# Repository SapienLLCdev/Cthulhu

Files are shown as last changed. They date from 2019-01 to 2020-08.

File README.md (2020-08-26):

## Cthulhu_Shield_Arduino

Cthulhu Shield

This is a library for using the Cthulhu Shield sensory substitution/augmentation development kit created by [Sapien LLC](http://sapienllc.com/). 

If you like what you see here, you can purchase a Cthulhu Shield [here!](https://sapienllc.com/shop/)

The Cthulhu Shield is an open-source Arduino Uno and Arduino Mega compatible sensory substitution/sensory augmentation device. It uses an 18 electrode grid to tactiley display signals on the tongue. The electrodes on the array can be activated with patterns of electrical pulses to depolarize nerve membranes in the tongue to create different types of touch sensations. You can use these touch sensations to draw shapes or simple images on the tongue, feel different sound frequencies, or receive turn by turn directions with your tongue.

Additionally, the Cthulhu Shield can sense whether or not your tongue is in contact with different electrodes using capacitive sensing. You can use the Cthulhu Shield to send keystrokes to your computer, control the cursor, or even control a mobility device. 

In this repository, we have provided a number of example projects to get you started with your Cthulhu, but we encourage you to experiment and build your own senses!

There are some awesome uses of sensory substitution already out there. For more information on these uses, or sensory substitution or augmentation in general, take a look at the links below. 
* [Brainport](https://www.youtube.com/watch?v=OKd56D2mvN0)
* [Wikipedia](https://en.wikipedia.org/wiki/Sensory_substitution)
* [Hear with your tongue](https://source.colostate.edu/words-mouth-csu-device-lets-hear-tongue/)
* [TedTalk](https://www.ted.com/talks/david_eagleman_can_we_create_new_senses_for_humans?language=en)

# Repository Contents:

* [Bare Minimum](https://github.com/SapienLLCdev/Cthulhu/tree/master/examples/BareMinimum)
* [Serial Input](https://github.com/SapienLLCdev/Cthulhu/tree/master/examples/SerialInput)
* [Accelerometer Example](https://github.com/SapienLLCdev/Cthulhu/tree/master/examples/accelerometer_Cthulhu_example)
* [GPS Directions](https://github.com/SapienLLCdev/Cthulhu/tree/master/examples/directions_example)
* [Make Patterns](https://github.com/SapienLLCdev/Cthulhu/tree/master/examples/make_patterns)
* [Thermal Camera](https://github.com/SapienLLCdev/Cthulhu/tree/master/examples/mega_heat_cam_with_shield)
* [Tactile Button](https://github.com/SapienLLCdev/Cthulhu/tree/master/examples/tactile_button_example)
* [Tactile Cursor](https://github.com/SapienLLCdev/Cthulhu/tree/master/examples/tactile_cursor)
* [Leonardo Tactile Cursor](https://github.com/SapienLLCdev/Cthulhu/tree/master/examples/Leonardo_tactile_cursor)
* [Tactile Keypad](https://github.com/SapienLLCdev/Cthulhu/tree/master/examples/tactile_keypad)
* [Cthulhu Camera Demo](https://github.com/SapienLLCdev/Cthulhu/tree/master/Android%20Examples/CthulhuCameraDemo)

# Cthulhu Shield Schematic:

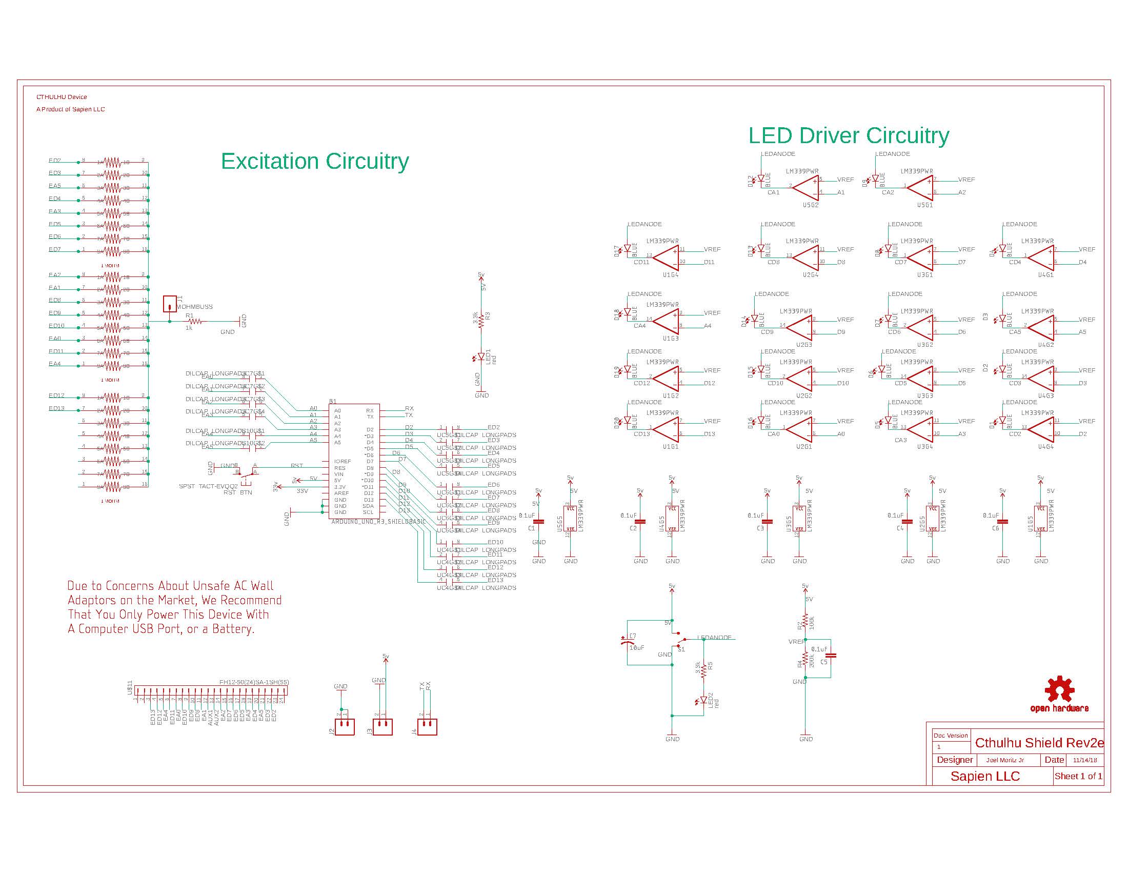
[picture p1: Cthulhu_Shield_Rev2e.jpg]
Cthulhu Shield Schematic
.

# How to Use the Cthulhu Shield:

**Power:**
The Cthulhu Shield is made to be powered by plugging it directly into an Arduino Uno or Mega, and connecting the arduino to a USB cable attached to a properly grounded computer, or a smartphone or external battery pack. Users should not power their Arduino/Cthulhu Shield system with an AC wall adaptor, as a small number of these adaptors are not properly grounded or are otherwise unsafe and can cause injury or death if used with any electronic device.

**Input:**
When used with an Arduino Uno, the Cthulhu Shield can receive information directly from the USB port connected to a computer or smartphone, or via broken out Serial pins (RX, TX) which can used to communicate with other Arduinos/microcontrollers, or embedded devices such as Bluetooth modules or sensors with serial outputs. With an Arduino Mega, the extra IO pins can be leveraged to receive Digital or Analog signals that can be used to change the tactile output of the Cthulhu Shield. 

**Output:**
When used with an Arduino Uno, the Cthulhu Shield can send information directly via USB port connected to a computer or smarptphone, or via broken out Serial pins (RX, TX) which can used to communicate with other Arduinos/microcontrollers, or embedded devices such as Bluetooth modules or sensors with serial outputs. With an Arduino Mega, the extra IO pins can be leveraged to send Digital or Analog signals to external devices. 

**Electrode Control:**
Different types of sensations can be created on different electrodes and tongue locations by changing the pattern of pulses generated on each electrode. This can be done with the Cthulhu.UpdateStimuli() function. A user changes values in six (6), eighteen (18) element arrays. The values in these arrays correspond to whether one of the 18 electrodes is on or off, and what type of pulse, and pattern of pulses, is created on each electrode. Changing these patterns changes the type and quality of the sensation perceived by the user. This library was adapted from [work by Kurt Kaczmarek](https://www.sciencedirect.com/science/article/pii/S1026309811001702) and altered for the needs of our early research at Sapien LLC.

**Tongue Position Sensing:**
During electrotactile stimulation with the Cthulhu Shield, the Arduino can quickly sense the electrical potential on a given electrode, which changes if the tongue is in contact with the electrode or not. Placing your tongue on certain electrodes but not others, or swiping your tongue across different electrodes, can be detected by the Arduino, which can then send serial information (or with minor hacking, keystrokes and HID signals) to a computer or smartphone via the USB port, or external Bluetooth modules. 

Currently, tongue-position-sensing is supported only on ADC enabled Arduino pins (A0-A5 on the Uno and Mega). Position sensing on digital only pins should be possible and may be implemented in the near future. 

# How to Use this Repository:

If you are new to Github, Sparkfun has created an [excellent Github tutorial](https://learn.sparkfun.com/tutorials/using-github/all). If you want to get up and running quickly, just take a look at the [Download ZIP](https://learn.sparkfun.com/tutorials/using-github/all#download-zip) section.

Similarly, if you are new to Arduino, Sparkfun once again has a great [guide to installing Arduino Libraries](https://learn.sparkfun.com/tutorials/installing-an-arduino-library). After downloading the .ZIP file of the library you want from Github, follow the instructions above to integrate it with the Arduino IDE.

Please see the README files in the examples linked above for more information on their specific implementations!

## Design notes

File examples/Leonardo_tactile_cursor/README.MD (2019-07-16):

## Using the Cthulhu Shield and Arduino Leonardo as a Full-Function Computer Mouse!

# Introduction:

The Cthulhu Shield and electrode array can be used to sense whether or not your tongue is in contact with certain electrodes. Combined with the electrotactile ability of the Cthulhu Shield, this can be used to create 'virtual' tactile buttons that can be pressed with the tongue. With with the HID library function of the arduino Leonardo, you can use the Cthulhu to control your computer cursor or type with your tongue!

This example will show you how to upload the example 'Leonardo_tactile_cursor.ino' sketch to an Arduino Leonardo with mounted Cthulhu Shield to use your tongue to mouse movements to your computer. You can also use the onscreen keyboard to type and send emails with your tongue! 

This example is considerably easier to use than the 'tactile_cursor' example. But requires an Arduino Leonardo.

[An video of the device being used can be found here](https://youtu.be/Bt2chGSGTl8)

[Instructions on how to control the cursor can be found here](https://github.com/SapienLLCdev/Cthulhu/blob/master/examples/Leonardo_tactile_cursor/Tongue%20mouse%20instructions.pdf)

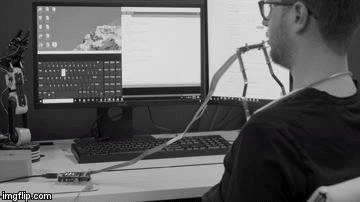
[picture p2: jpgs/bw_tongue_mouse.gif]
Game_Control


# Required Materials:

* Cthulhu Shield

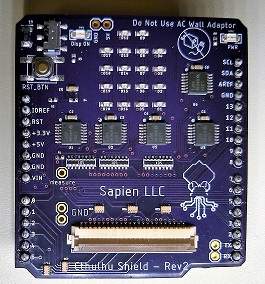
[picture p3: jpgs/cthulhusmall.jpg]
Cthulhu Shield

* Arduino Leonardo or compatible clone with Atmega32U4 microcontroller.

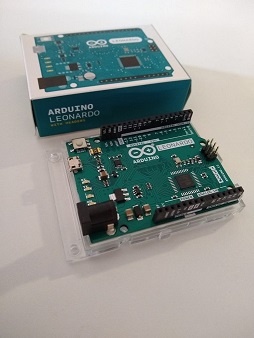
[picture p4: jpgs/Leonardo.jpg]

* USB A to B Cable

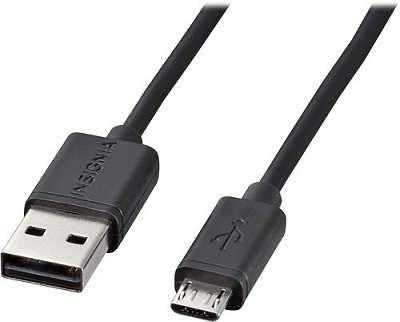
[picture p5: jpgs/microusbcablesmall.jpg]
USB A to micro B cable


* One 18 Channel flexible electrode array from Sapien LLC

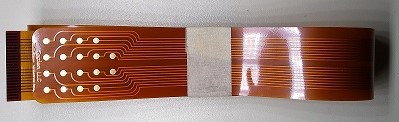
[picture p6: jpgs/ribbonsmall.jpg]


# Required Software:
* This library
* [Arduino IDE](https://www.arduino.cc/en/Main/Software)

# Hardware Assembly:
Install Cthulhu Shield onto Arduino Leonardo and attach the USB cable and electrode array. 

# PC Setup:
For setup on Windows, follow the instructions below. If you have a Mac, please see the section entitled [Mac Setup](#mac-setup) further down the page. 

Open Arduino IDE. Once you have installed the Cthulhu Shield library (see 'Install Library' at end) go to **file**>**examples**>**Cthulhu-master** and open the **Leonardo_tactile_cursor** example sketch.

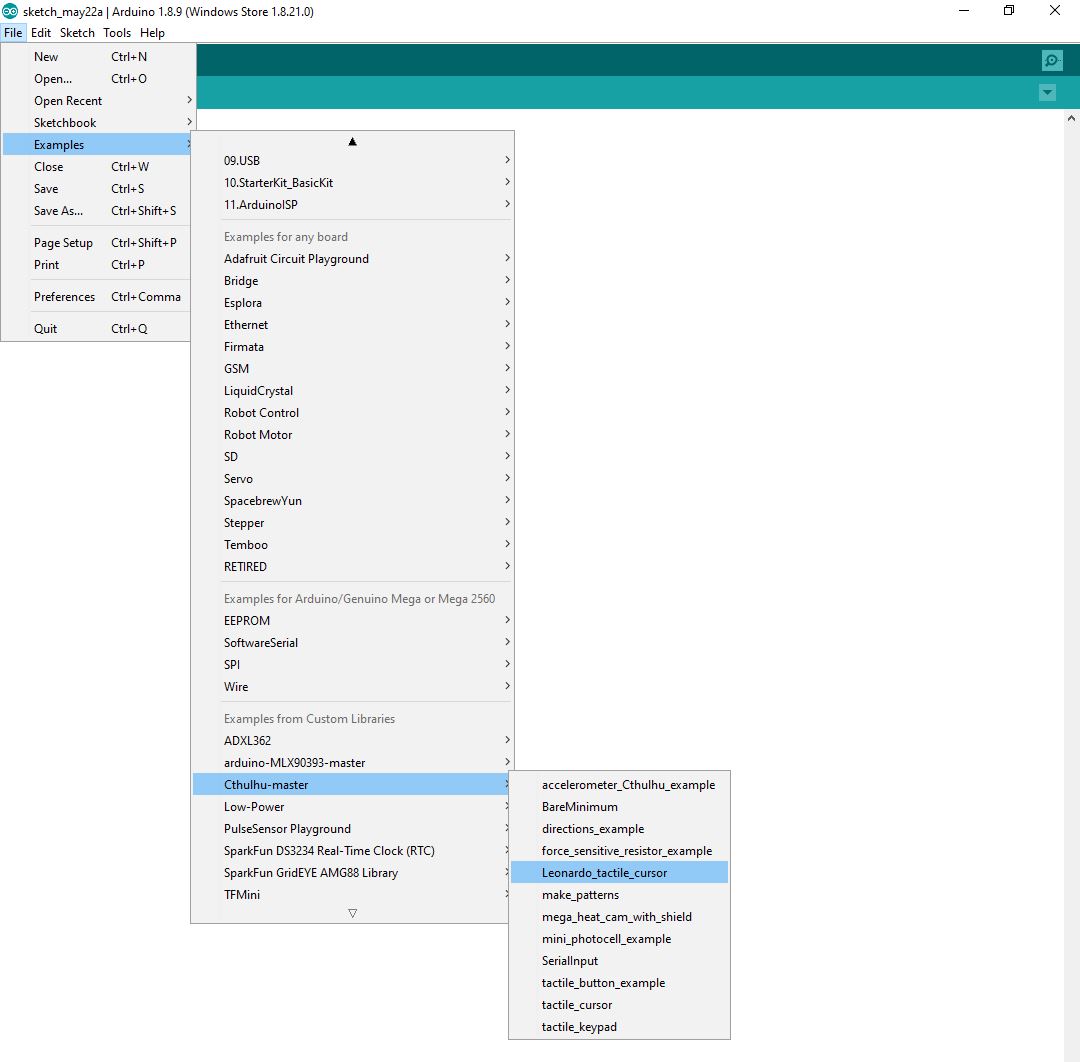
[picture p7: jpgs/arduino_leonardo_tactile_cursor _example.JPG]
example


Set your board and serial port from the **tools** dropdown menu and upload the sketch to your Arduino Leonardo.

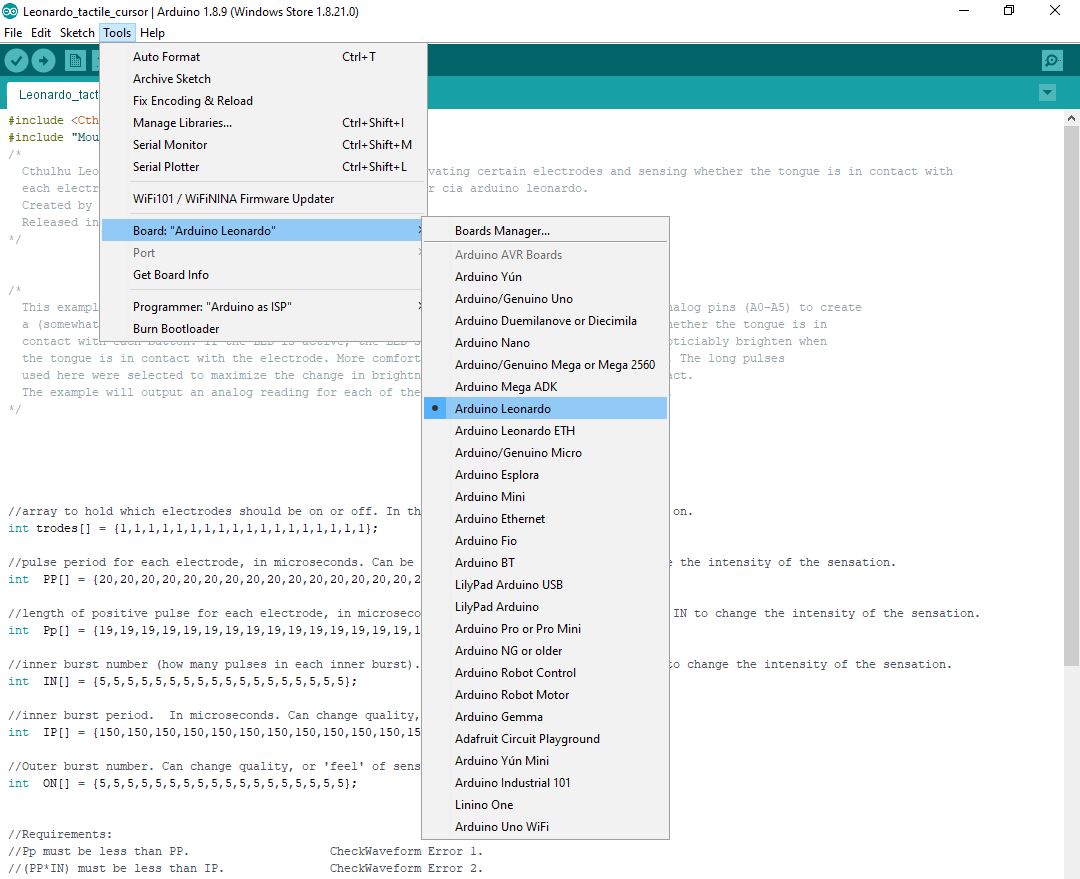
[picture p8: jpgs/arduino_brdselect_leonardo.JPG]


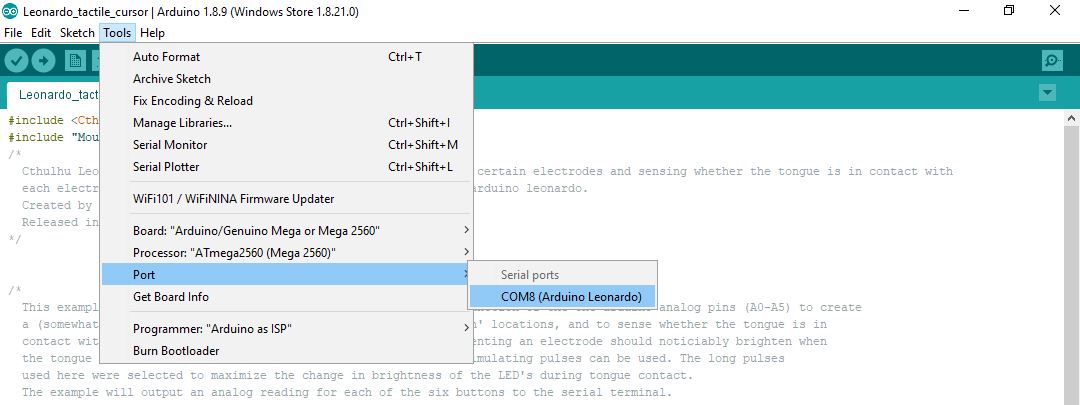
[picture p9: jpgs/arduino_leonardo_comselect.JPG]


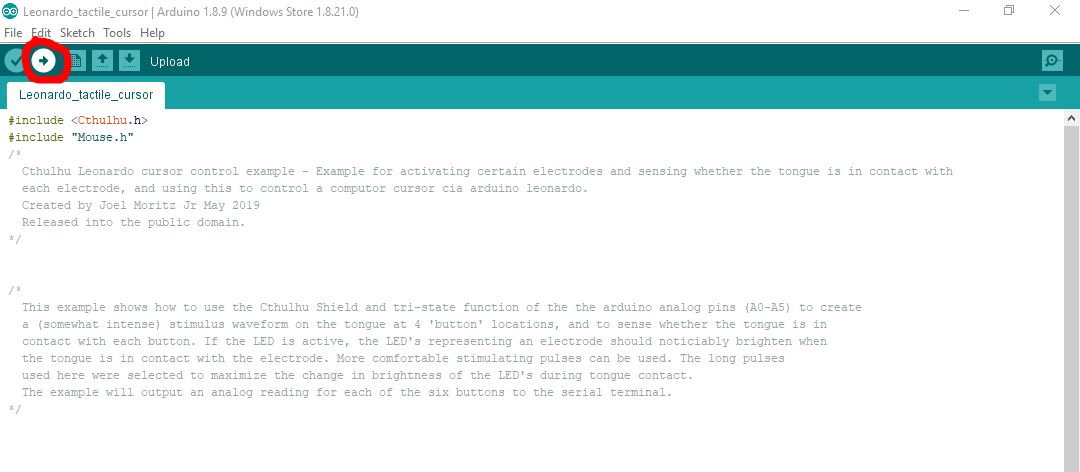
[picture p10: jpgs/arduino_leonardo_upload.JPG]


If you havent already, carefully lift the latch of the ZIF connector, insert the electrode array gold side down, and close the latch. 

* Use the tip of your tongue to press the tactile 'buttons' on the electrodes at the front, back , and both sides of the array. The LED's on the Cthulhu Shield will (very slightly) change brightness when your tongue is contacting them.
* To click, flatten your tongue against the array (and the roof of your mouth) with a slapping motion to contact all the electrodes, then pull your tongue off the array. Double clicking works similarly. Clicking will activate all LED's on the array at once to give you tactile and visual feedback.
* To right-click, flatten your tongue against all electrodes as described above, and hold your tongue against all electrodes for about 2 seconds, then release. The appropriate right-click menu should pop up when released. 
* To click-drag/click-and-hold (moving a window, or using a scrollbar, etc), Flatten your tongue against all electrodes to click, and hold your tongue against the array while sliding your tongue to the desired directional button.

You can enable the oncsreen keyboard in the windows control panel if you want to try typing with your tongue! 

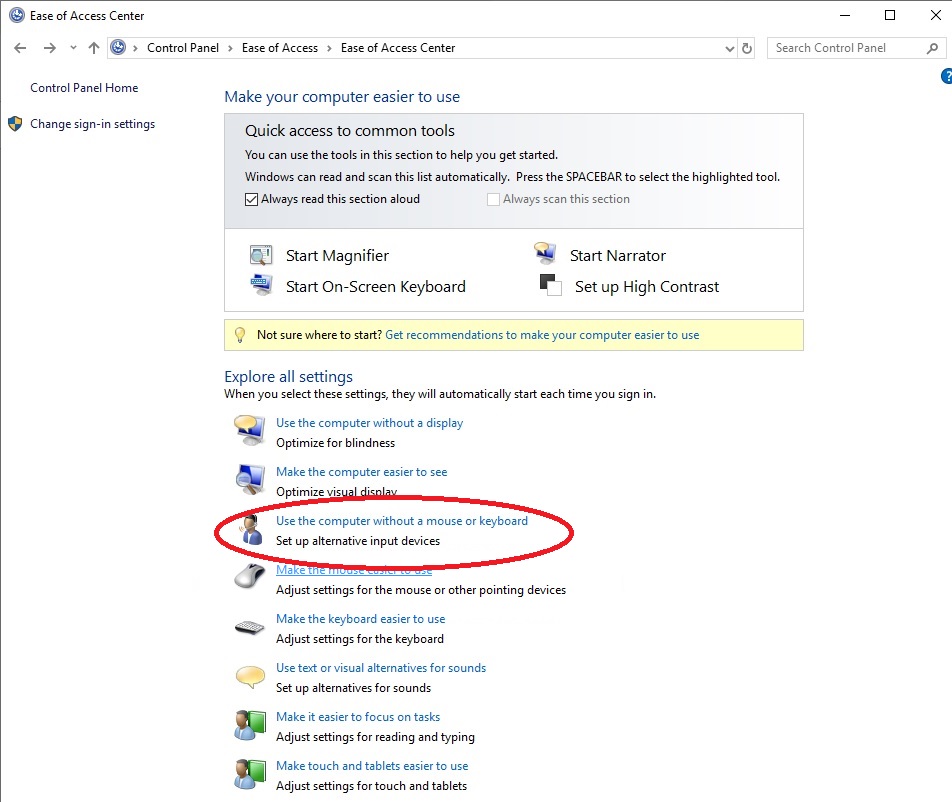
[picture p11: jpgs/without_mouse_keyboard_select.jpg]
key1


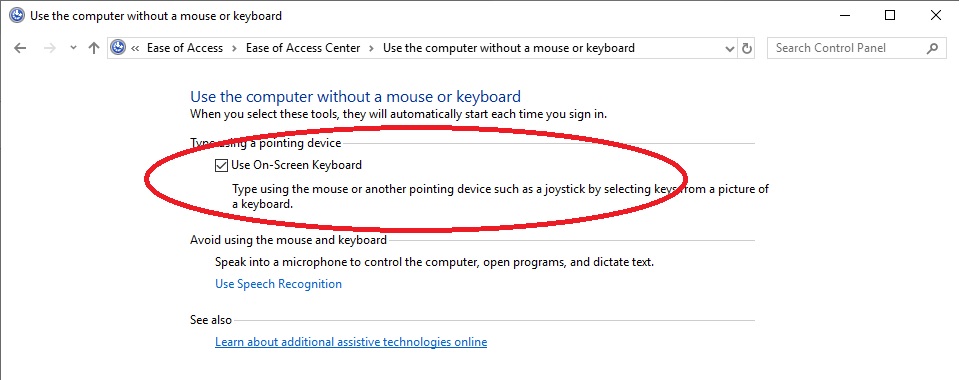
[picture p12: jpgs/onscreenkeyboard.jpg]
key2


# Going Further:

# Acknowledgments: 

# Install Library:

Right now, the easiest way to install the Cthulhu library is by downloading the Zip file from github, and manually adding it from the arduino 'sketch' dropdown menu.

Navigate to the Cthulhu repo main page and download the zip file.

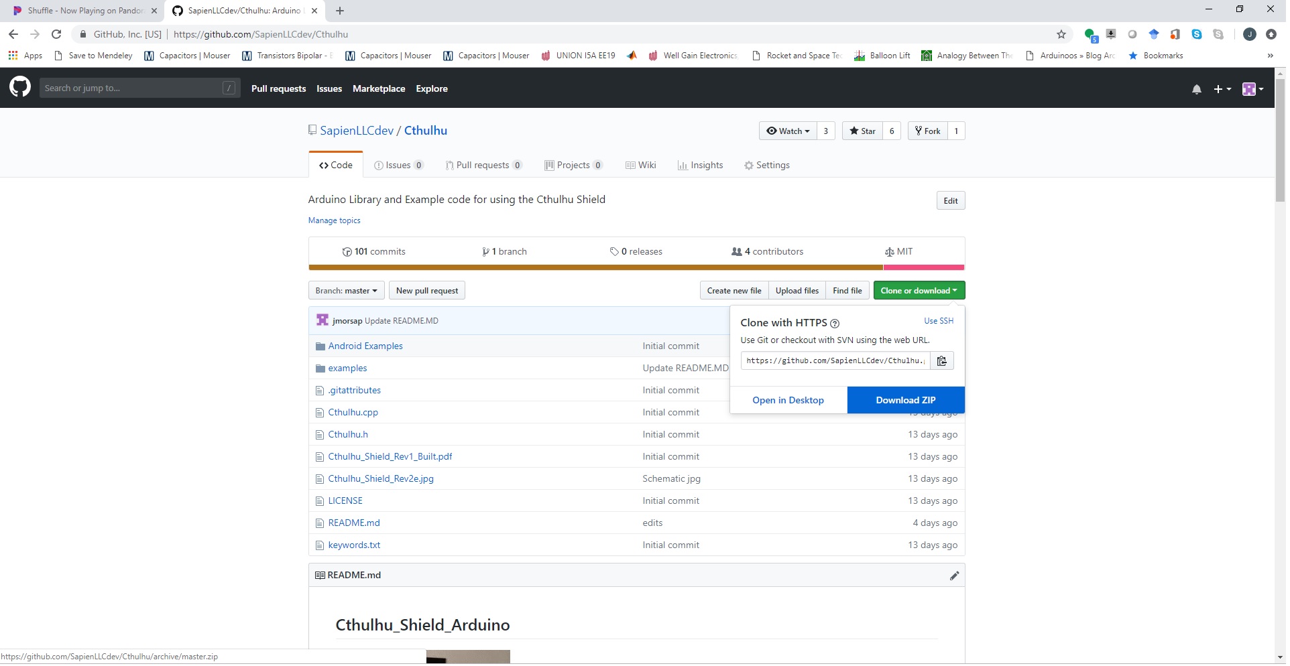
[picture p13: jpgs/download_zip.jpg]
zip


Open Arduino and select **Include Library** > **Add .ZIP Library** from the **Sketch** dropdown menu.

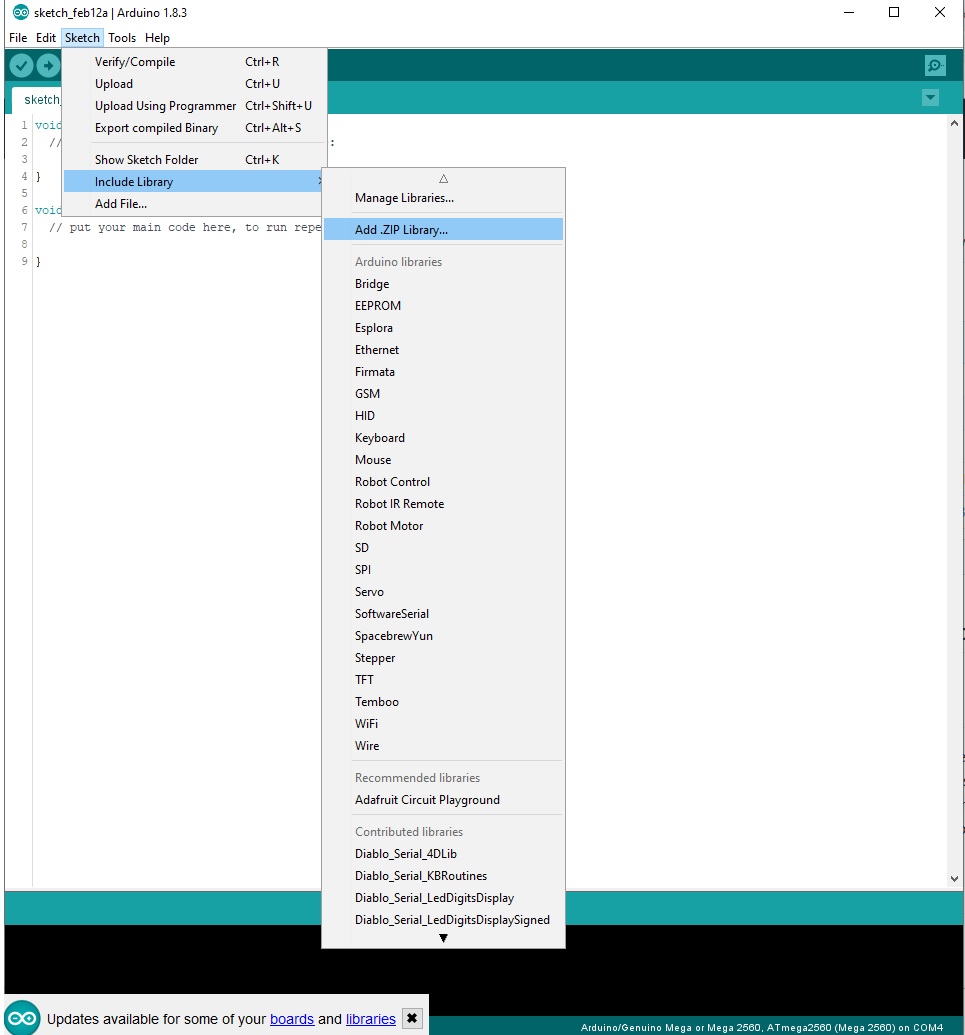
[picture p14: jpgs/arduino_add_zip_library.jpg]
add library


Navigate to the zip file you downloaded and select it (probably your 'Downloads' folder). 

The library should now be installed.

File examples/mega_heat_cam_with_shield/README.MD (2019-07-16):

## Using the Cthulhu Shield, Arduino Mega, and the SparkFun GRID-Eye Infrared Array (Qwicc) to Sense Warm Objects With Your Tongue!

# Introduction

This example illustrates the use of the Cthulhu as a sensory substitution device paired with the Quicc GRID-Eye Infrared Array to sense the warmth of objects. When a warm object is sensed by the Infrared Array, the LEDs on the Cthulhu will light up, and the corresponding electrodes on the removable flexible array will be stimulated.

# Required Materials:

* Cthulhu Shield

Cthulhu_Shield

* Arduino Mega or compatible clone

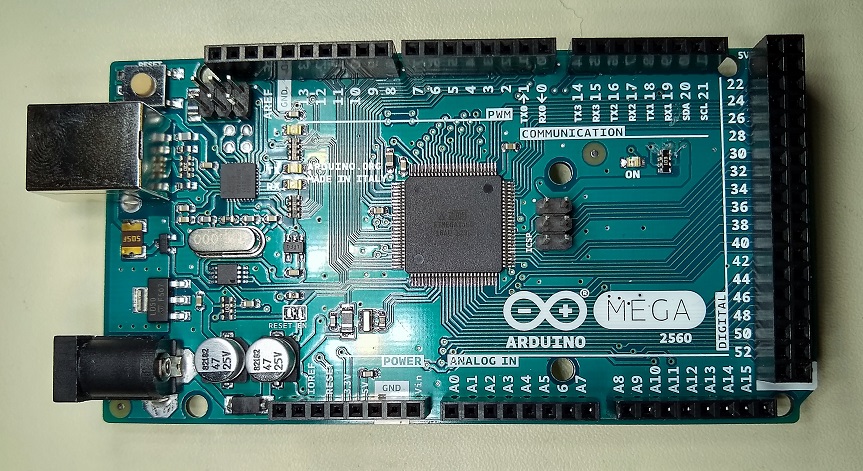
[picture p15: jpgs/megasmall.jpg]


* SparkFun Grid-EYE Infrared Array Breakout - AMG8833 (Qwiic)

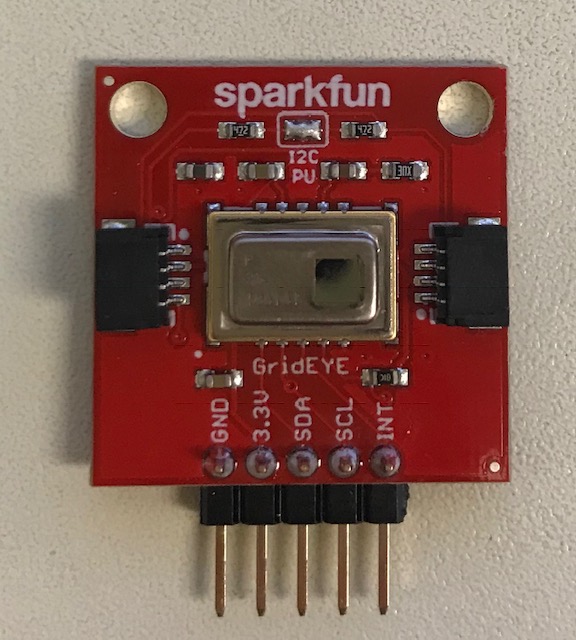
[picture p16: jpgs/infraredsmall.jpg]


* SparkFun Logic Level Converter - Bi-Directional

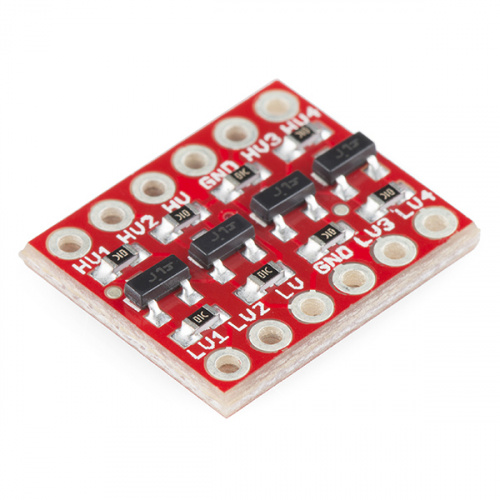
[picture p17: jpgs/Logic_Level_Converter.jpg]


* USB A to B Cable

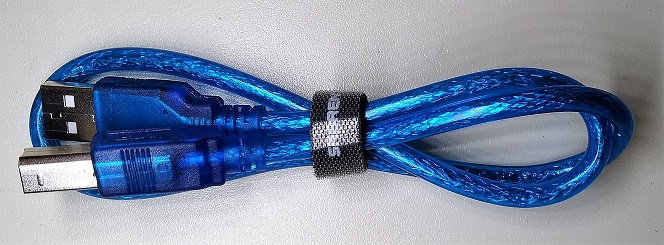
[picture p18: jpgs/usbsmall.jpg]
USB A to B Cable


* One 18 Channel flexible electrode array from Sapien LLC

Cthulhu Shield

# Required Software
* This library (Directions on how to install below)
* [Arduino IDE](https://www.arduino.cc/en/Main/Software)
* [GridEYE Library](https://github.com/sparkfun/SparkFun_GridEYE_Arduino_Library).

If you do not know how to install an Arduino library, refer to the "How to Use this Repository" section [in the README](https://github.com/SapienLLCdev/Cthulhu). 

# Hardware Assembly:
Install Cthulhu Shield onto Arduino Uno or Arduino Mega and attach the USB cable and electrode array. 

# Quicc GRID-Eye Infrared Array setup with Arduino Mega, Cthulhu Shield, and Logic Level Converter

| Cthulhu Shield/Mega | High Side of Converter | Low side of converter | Infrared Camera |
| ------------------- | ---------------------- | --------------------- | --------------- |
| 3.3V  | N/A  | LV  | 3.3V  |
| 5V  | HV  | N/A  | N/A  |
| GND  | GND  | GND  | GND  |
| Pin 20 (SDA)  | HV1  | LV1  | SDA  |
| Pin 21 (SCL)  | HV2  | LV2  | SCL  |

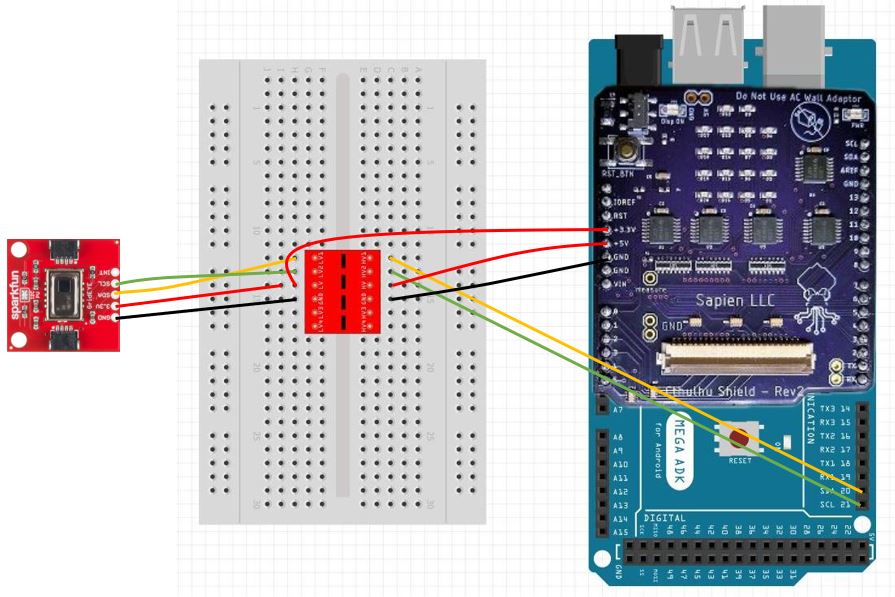
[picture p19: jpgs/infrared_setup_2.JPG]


The logic level converter is used in this example because the infrared camera uses 3.3V and the Arduino mega uses 5V. The 5V goes into the HIGH (HV) side of the converter and the 3.3V goes into the LOW (LV) side, as pictured above.

# Example:
Open Arduino IDE. Once you have installed the Cthulhu Shield library (see 'Install Library' at end) go to **file**>**examples**>**Cthulhu-master** and open the **mega_heat_cam_with_shield** example sketch.

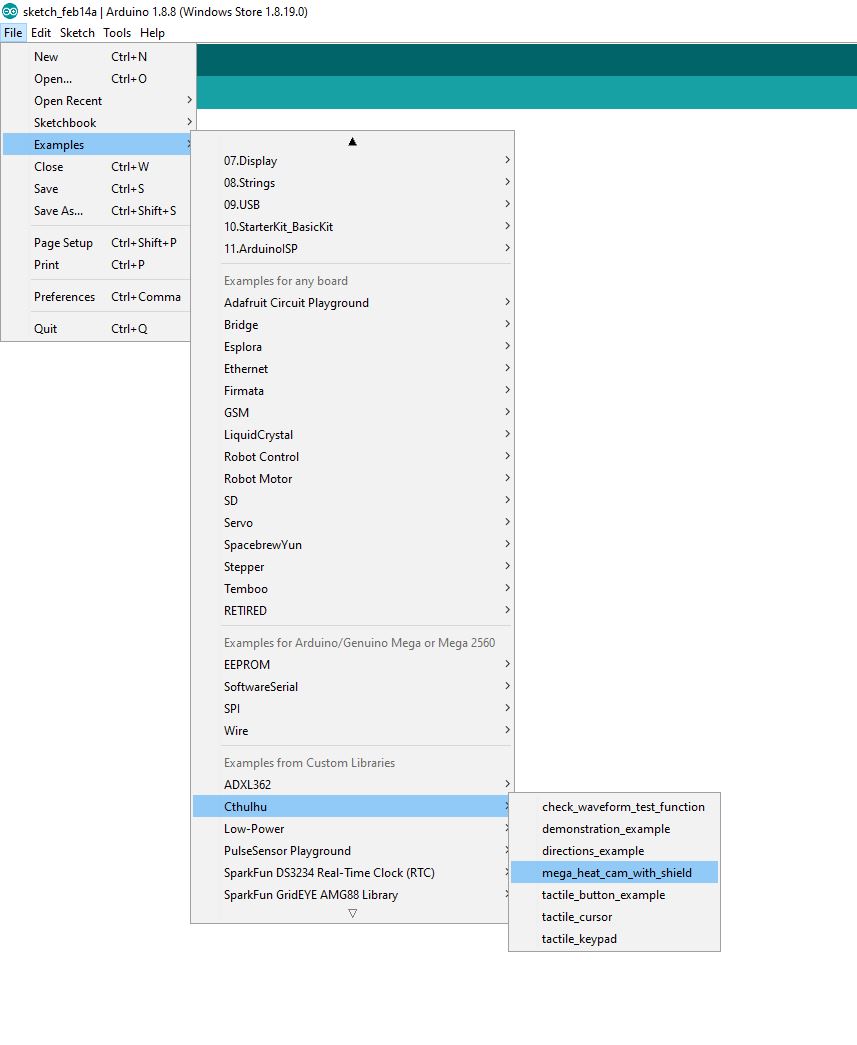
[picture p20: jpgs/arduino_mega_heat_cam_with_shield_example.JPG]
example


Set your board and serial port from the **tools** dropdown menu and upload the sketch to your Arduino Uno or Mega.

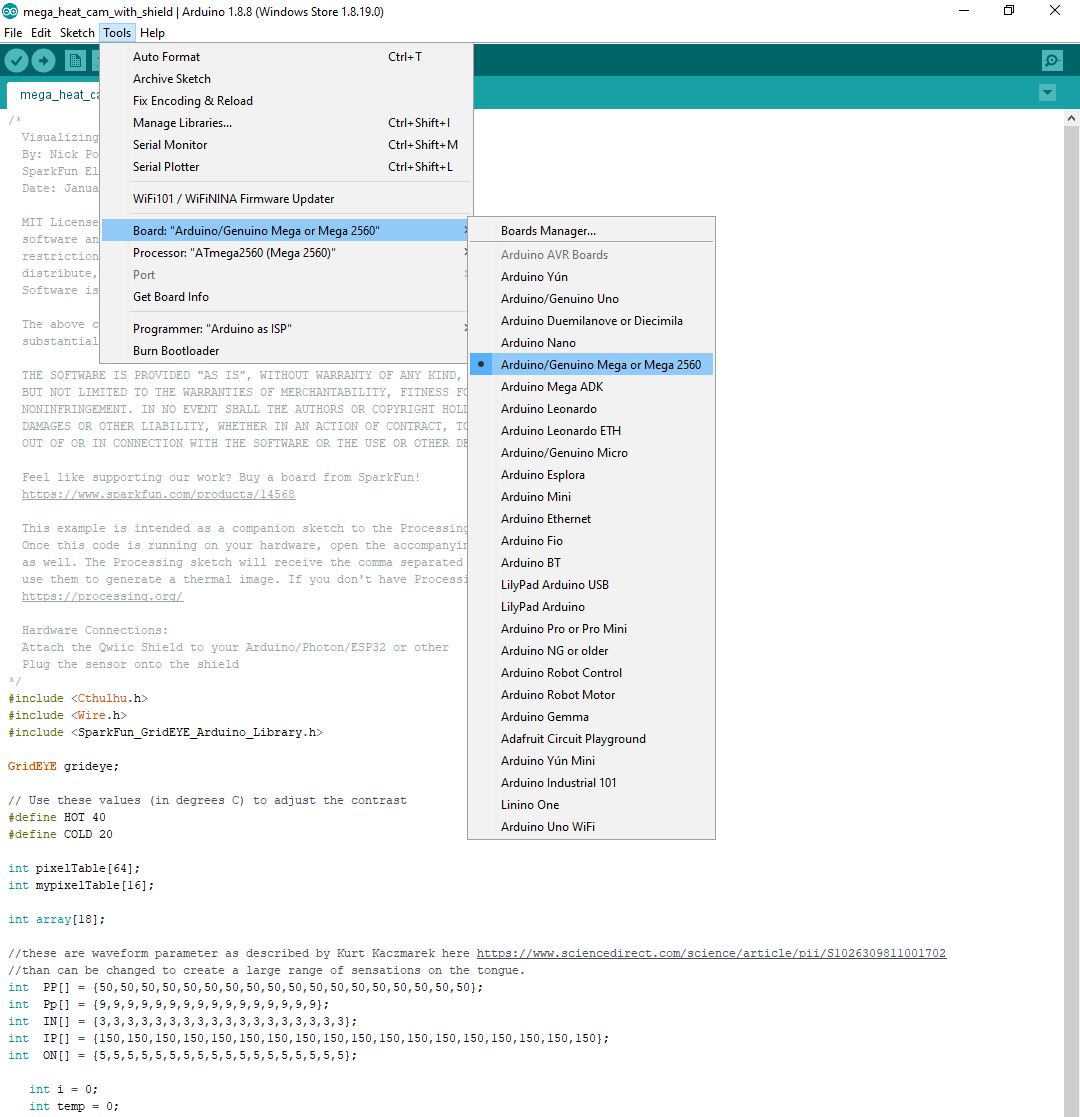
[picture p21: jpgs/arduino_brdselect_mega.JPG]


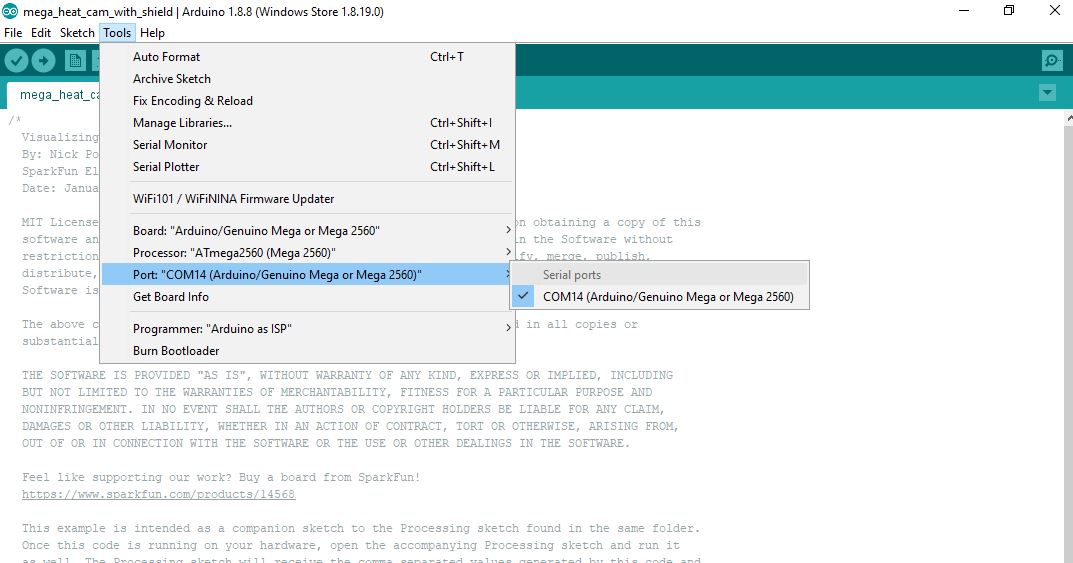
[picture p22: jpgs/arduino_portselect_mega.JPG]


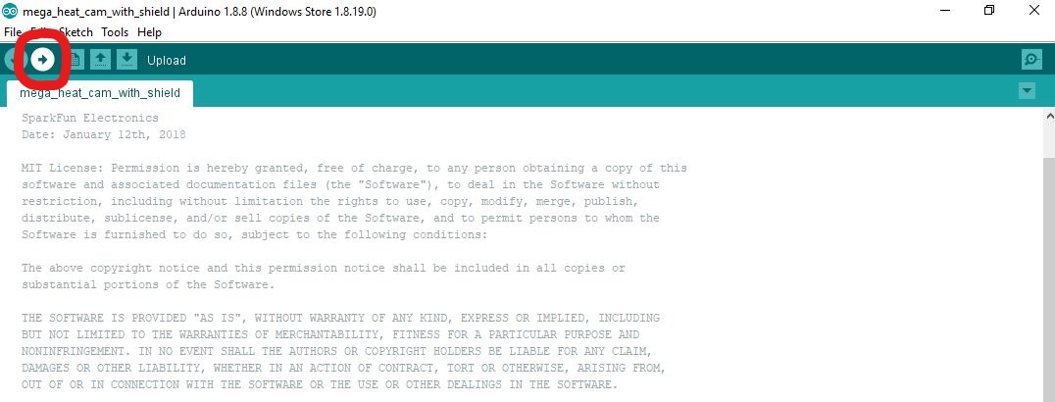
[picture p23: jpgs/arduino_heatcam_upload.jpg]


If everything has been setup correctly, when you wave a warm object (such as your hand) over the SparkFun GRID-Eye Infrared Array sensor, the LEDs on the Cthulhu Shield will respond by lighting up. If you wave a cold object over the sensor, then no LEDs will light up. If the 18 Channel flexible electrode array from Sapien LLC has been connected to the Cthulhu Shield, the electrodes on the flexible array will be stimulated in response to warm objects. 

# Install Library:

Right now, the easiest way to install the Cthulhu library is by downloading the Zip file from github, and manually adding it from the arduino 'sketch' dropdown menu.

Navigate to the Cthulhu repo main page and download the zip file.

zip

Open Arduino and select **Include Library** > **Add .ZIP Library** from the **Sketch** dropdown menu.

add library

Navigate to the zip file you downloaded and select it (probably your 'Downloads' folder). 

The library should now be installed.

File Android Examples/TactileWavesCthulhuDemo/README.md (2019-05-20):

Tactile Waves Cthulhu Demo
==========================
This app shows how the [Tactile Waves Android library](https://github.com/Funkatronics/TactileWaves "Tactile Waves") can be used with the Cthulhu Shield to build a sound-to-touch sensory substitution system.

Tactile Waves is used to capture and process audio from the devices microphone to extract its fundamental frequency (pitch) and formant frequencies. These frequencies are drawn to the screen for visualization. 

An Arduino equipped with a Cthulhu Shield can be connected to the app via USB or Bluetooth (using the 3-dot overflow menu on the app's toolbar). When connected, the formant frequencies will be mapped and sent to the Cthulhu LEDs/electrodes.

Installation
------------
The easiest way to install this app is via the Google Play Store here.~~ https://play.google.com/store/apps/developer?id=SapienLLC&hl=en_US

Alternatively, the APK provided in this folder can be installed by enabling "Unknown Sources" in your devices security settings. With this setting enabled, you will be able to open the APK file on your device and Android will begin the installation automatically. 

You can also clone this repository to a folder on your computer and build the APK yourself. 

Credits
-------
Built by Marco Martinez ([Funkatronics](https://github.com/funkatronics "Funkatronics GitHub")) with support from Sapien, LLC and CSU Ventures.

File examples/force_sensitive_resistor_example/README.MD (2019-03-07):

## Using the Cthulhu Shield, Arduino Mega, and the SparkFun Force Sensitive Resistor to Feel Changes in Force with your Tongue!

# Introduction

This example illustrates the use of the Cthulhu as a sensory substitution device paired with the SparkFun Force Sensitive Resistor to feel changes in force intensity. The greater amount of force placed on the Force Sensitive Resistor, the more intense the stimulation experience will be.

# Required Materials:

* Cthulhu Shield

Cthulhu_Shield

* Arduino Mega or compatible clone

Cthulhu Shield

* SparkFun Force Sensitive Resistor 0.5"

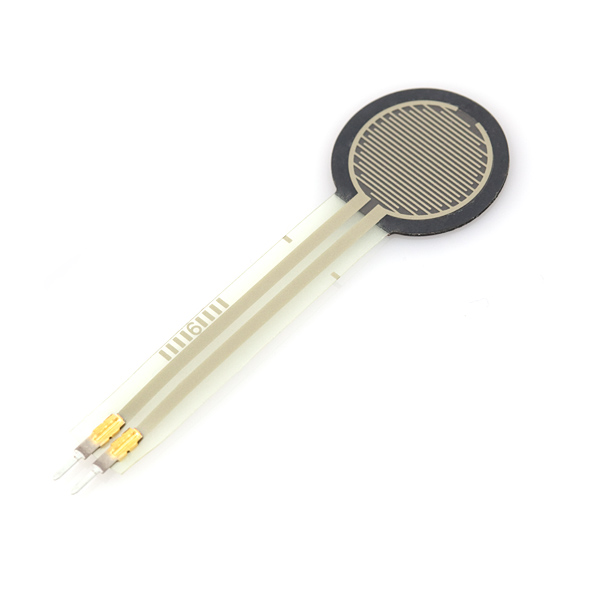
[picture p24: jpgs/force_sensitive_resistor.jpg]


* 3.3kΩ Resistor

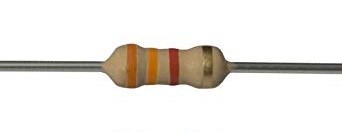
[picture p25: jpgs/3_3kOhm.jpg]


* Breadboard

Cthulhu_Shield

* USB A to B Cable

USB A to B Cable

* One 18 Channel flexible electrode array from Sapien LLC

Cthulhu Shield

# Required Software
* This library (Directions on how to install below)
* [Arduino IDE](https://www.arduino.cc/en/Main/Software)

If you do not know how to install an Arduino library, refer to the "How to Use this Repository" section [in the README](https://github.com/SapienLLCdev/Cthulhu). 

# Hardware Assembly:
Install Cthulhu Shield onto Arduino Uno or Arduino Mega and attach the USB cable and electrode array. 

# Force Sensitive Resistor Setup with Mega and Cthulhu Shield 

Cthulhu_Shield

For this example, a 3.3kΩ resistor was used. Refer to the SparkFun Force Sensitive Resistor hookup guide [here](https://learn.sparkfun.com/tutorials/force-sensitive-resistor-hookup-guide?_ga=2.62589669.834921711.1551994825-586526424.1528213955) if more reference is needed.

# Example:
Open Arduino IDE. Once you have installed the Cthulhu Shield library (see 'Install Library' at end) go to **file**>**examples**>**Cthulhu-master** and open the **force_sensitive_resistor_example** example sketch.

example

Set your board and serial port from the **tools** dropdown menu and upload the sketch to your Arduino Uno or Mega.

example

example

example

If everything has been setup correctly, when the example is uploaded, no electrodes should be stimuluated initially. Once a force is applied to the Force Sensitive Resistor, by squeezing it with your fingers for example, the electrodes will be stimulated in an "X" pattern. The greater amount of force applied (the harder you squeeze) the greater intensity of the stimulus. Once the force applied is reduced, the intensity of the stimuluation will decrease. 
 
# Install Library:

Right now, the easiest way to install the Cthulhu library is by downloading the Zip file from github, and manually adding it from the arduino 'sketch' dropdown menu.

Navigate to the Cthulhu repo main page and download the zip file.

zip

Open Arduino and select **Include Library** > **Add .ZIP Library** from the **Sketch** dropdown menu.

add library

Navigate to the zip file you downloaded and select it (probably your 'Downloads' folder). 

The library should now be installed.

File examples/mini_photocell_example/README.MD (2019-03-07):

## Using the Cthulhu Shield, Arduino Mega, and the SparkFun Mini Photocell to Feel Light with your Tongue!

# Introduction

This example illustrates the use of the Cthulhu as a sensory substitution device paired with the SparkFun Mini Photocell to feel changes in light intensity. The more intense the light on the Mini Photocell, the more intense the stimulation experience will be.

# Required Materials:

* Cthulhu Shield

Cthulhu_Shield

* Arduino Mega or compatible clone

Cthulhu Shield

* SparkFun Mini Photocell

Cthulhu_Shield

* Breadboard

Cthulhu_Shield

* 1kΩ Resistor

Cthulhu_Shield

* USB A to B Cable

USB A to B Cable

* One 18 Channel flexible electrode array from Sapien LLC

Cthulhu Shield

# Required Software
* This library (Directions on how to install below)
* [Arduino IDE](https://www.arduino.cc/en/Main/Software)

If you do not know how to install an Arduino library, refer to the "How to Use this Repository" section [in the README](https://github.com/SapienLLCdev/Cthulhu). 

# Hardware Assembly:
Install Cthulhu Shield onto Arduino Uno or Arduino Mega and attach the USB cable and electrode array. 

# Mini Photocell setup with Mega and Cthulhu Shield 

Cthulhu_Shield

For this example, a 1kΩ resistor was used. Refer to the SparkFun Mini Photocell setup guide [here](https://learn.sparkfun.com/tutorials/photocell-hookup-guide/all) if more reference is needed.

# Example:
Open Arduino IDE. Once you have installed the Cthulhu Shield library (see 'Install Library' at end) go to **file**>**examples**>**Cthulhu-master** and open the **mini_photocell_example** example sketch.

example

Set your board and serial port from the **tools** dropdown menu and upload the sketch to your Arduino Uno or Mega.

example

example

example

If everything has been setup correctly, when the example is uploaded, the electrodes should be stimulated in an "x" pattern. If the light intensity is increased on the photocell by shining a flashlight on it, for example, the intensity of the stimulus will increase. If the light intesnity is decreased by turning off the lights or putting a solid object over the photocell, for example, the intensity of the stimulus will decrease.

For this example a 1kΩ resistor was used, but a 1kΩ up to a 10kΩ resistor can be used with the photocell. Just know that changing the resistance will change the amount of voltage experienced by the photocell.
 
# Install Library:

Right now, the easiest way to install the Cthulhu library is by downloading the Zip file from github, and manually adding it from the arduino 'sketch' dropdown menu.

Navigate to the Cthulhu repo main page and download the zip file.

zip

Open Arduino and select **Include Library** > **Add .ZIP Library** from the **Sketch** dropdown menu.

add library

Navigate to the zip file you downloaded and select it (probably your 'Downloads' folder). 

The library should now be installed.

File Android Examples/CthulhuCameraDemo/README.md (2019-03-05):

Cthulhu Camera Demo
===================
This example app uses a simple frame difference method to detect motion within each frame from an Android device's front or back camera. This motion is then mapped to the 4x4 grid of electrodes on the Cthulhu Shield, connected via USB.

An evenly spaced 4x4 grid is drawn over the video stream. If the amount of motion (the difference between the previous and current frame) within one tile of the grid exceeds a threshold value, the cooresponding LED/electrode on the Cthulhu is activated. The user can adjust this threshold value using the 3-dot overflow menu on the apps toolbar. Lower threshold values will make the motion detection more sensitive (a smaller amount of motion will trigger an electrode). 

Installation
------------
The easiest way to install this app is via the Google Play Store, [here](https://play.google.com/store/apps/details?id=funkatronics.code.cthulhucamerademo&hl=en "CthulhuCameraMotionDemo")

Alternatively, the APK provided in this folder can be installed by enabling "Unknown Sources" in your devices security settings. With this setting enabled, you will be able to open the APK file on your device and Android will begin the installation automatically. 

You can also clone this repository to a folder on your computer and build the APK yourself. 

Credits
-------
Built by Marco Martinez ([Funkatronics](https://github.com/funkatronics "Funkatronics GitHub")) with support from Sapien, LLC

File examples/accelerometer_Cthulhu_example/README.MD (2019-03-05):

## Using the Cthulhu Shield, Arduino Mega, and the SparkFun Triple Axis Accelerometer to Feel Movement With Your Tongue!

# Introduction

This example illustrates the use of the Cthulhu Shield as a sensory substitution device paired with the SparkFun Triple Axis Accelerometer to feel movement on the positive and negative X and Y axes. When the accelerometer is moved in the positive or negative direction of the axes, the corresponding electrodes on the removable flexible array will be stimulated.

# Required Materials:

* Cthulhu Shield

Cthulhu_Shield

* Arduino Mega or compatible clone

Cthulhu Shield

* SparkFun Triple Axis Accelerometer Breakout - ADXL362

Cthulhu_Shield

* USB A to B Cable

USB A to B Cable

* One 18 Channel flexible electrode array from Sapien LLC

Cthulhu Shield

# Required Software
* This library (Directions on how to install below)
* [Arduino IDE](https://www.arduino.cc/en/Main/Software)
* [ADXL362](https://github.com/annem/ADXL362)

If you do not know how to install an Arduino library, refer to the "How to Use this Repository" section [in the README](https://github.com/SapienLLCdev/Cthulhu). 

# Hardware Assembly:
Install Cthulhu Shield onto Arduino Uno or Arduino Mega and attach the USB cable and electrode array. 

# Triple Axis Accelerometer setup with mega and Cthulhu Shield 

On Triple Axis Accelerometer  |    On Cthulhu Shield/Arduino MEGA
-----------------------------|----------------------------------
GND	            			 |              GND
V+	           				 |             3.3V
SCK	           				 |            Pin 52
MOSI	      				 |            Pin 51
MISO						 |			Pin 50
CS              			 |				Pin 53

* Labeled Pins on Triple Axis Accelerometer

Cthulhu_Shield

* Full Setup

Cthulhu_Shield

# Example:
Open Arduino IDE. Once you have installed the Cthulhu Shield library (see 'Install Library' at end) go to **file**>**examples**>**Cthulhu-master** and open the **accelerometer_Cthulhu_example** example sketch.

example

Set your board and serial port from the **tools** dropdown menu and upload the sketch to your Arduino Uno or Mega.

example

example

example

If everything has been setup correctly, when the example is uploaded, if the accelerometer is tilted up towards the user (+X), down away from the user (-X), down to the right (+Y), and down toward the left (-Y), the corresponding elecrodes will be stimulated. This allows for the user to feel the movement in the different directions with their tongue. The further in the direction the accelerometer is tilted, the more intense feeling the stimulation will be. 

Tilted Axis  |  Stimulated Electrodes
-----------------------------|----------------------------------
+X	            			 |                3, 4
-X	           				 |               15, 16
+Y	           				 |              9, 13
-Y	      				 |              6, 10

* Electrode Numbers on the Cthulhu Shield
<pre>
	{   0, 1   },
	{2, 3, 4, 5},
	{6, 7, 8, 9},
	{10,11,12,13},
	{14,15,16,17}
</pre>

# Install Library:

Right now, the easiest way to install the Cthulhu library is by downloading the Zip file from github, and manually adding it from the arduino 'sketch' dropdown menu.

Navigate to the Cthulhu repo main page and download the zip file.

zip

Open Arduino and select **Include Library** > **Add .ZIP Library** from the **Sketch** dropdown menu.

add library

Navigate to the zip file you downloaded and select it (probably your 'Downloads' folder). 

The library should now be installed.

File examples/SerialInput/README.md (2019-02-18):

## Activing Electrodes on the Cthulhu Shield Electrode Array Using Serial Input

# Introduction
This example shows how to activate electrodes on the Cthulhu Shield electrode array using serial input (from USB port, or an external device like a bluetooth module or another arduino).

Stimulation parameters are pre-set, and the serial input simply turns different electrodes on or off.

This eample works with the CthulhuCameraMotionDemo android app available on the android store: 
(https://play.google.com/store/apps/details?id=funkatronics.code.cthulhucamerademo) and the Cthulhu Tactile waves demo app soon to be available.

# Required Materials:

* Cthulhu Shield

Cthulhu_Shield

* Arduino Uno or compatible clone

Cthulhu Shield

* USB A to B Cable

USB A to B Cable

* One 18 Channel flexible electrode array from Sapien LLC

Cthulhu Shield

# Required Software
* [Arduino IDE](https://www.arduino.cc/en/Main/Software)
* This library (Directions on how to install below)
* [Coolterm-optional](http://freeware.the-meiers.org/)

# Hardware Assembly:
Install Cthulhu Shield onto Arduino Uno or Arduino Mega and attach the USB cable and electrode array. 

# Example:
Open Arduino IDE. Once you have installed the Cthulhu Shield library (see 'Install Library' at end) go to **file**>**examples**>**Cthulhu-master** and open the **SerialInput** example sketch.

example

Set your board and serial port from the **tools** dropdown menu and upload the sketch to your Arduino Uno or Mega.

example

example

The Serial Input example is ready to be uploaded.

example

Next, the app CoolTerm.exe can be used to activate individual electrodes on the Cthulhu. After opening CoolTerm, connect to the serial port.

example

Open the **Send String** window by going to **connection**>**Send String**. The Send String window will now be displayed.

example

In the Send String window, select **Hex**.

example

You can now manually input with hexadecimal numbers which electrodes you'd like to active. There are electrodes 1-18.

Hexadecimal and Decimal Numbers
--------------------------------
    01 = 1     |      0a = 10
	02 = 2     |      0b = 11                
    03 = 3     |      0c = 12
    03 = 3     |      0d = 13
    04 = 4     |      0e = 14
    05 = 5     |      0f = 15
    06 = 6     |      10 = 16
    07 = 7     |      11 = 17
    08 = 8     |      12 = 18
    09 = 9

For example: If you type 01 02 03 0a 12 00 and press **Send**, it will turn on electrodes 0, 1, 2, 9, and 17 in the array. 
Always include 00 at the end of the string.

example

To deactive all electrodes type **00 00** and press send.

# Install Library:

Right now, the easiest way to install the Cthulhu library is by downloading the Zip file from github, and manually adding it from the arduino 'sketch' dropdown menu.

Navigate to the Cthulhu repo main page and download the zip file.

zip

Open Arduino and select **Include Library** > **Add .ZIP Library** from the **Sketch** dropdown menu.

add library

Navigate to the zip file you downloaded and select it (probably your 'Downloads' folder). 

The library should now be installed.

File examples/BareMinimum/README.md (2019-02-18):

## How to Use Sapien LLC's Cthulhu Shield to Electrotactiley Stimulate the Tongue

# Introduction
This example shows how to use Sapien LLC's Cthulhu Sheild to electrotactiley stimulate the tongue. In this example, one electrode is set active, and five stimulation parameters are set. The Cthulhu library is initialized, and serial output is enabled. 
  
The CheckWaveform function is used to verify that we have entered a valid waveform for all electrodes, if the paramters we entered are OK, then the stimulus waveform is updated (UpdateStimuli), and the pulsetrain is sent to the active electrodes (Stimulate) for one stimulation cycle (36ms). 

If the waveform is invalid, the error code is printed to the serial monitor and the stimulus is not updated or produced. 

This loops indefinitely.

# Required Materials:

* Cthulhu Shield

Cthulhu_Shield

* Arduino Uno or compatible clone

Cthulhu Shield

* USB A to B Cable

USB A to B Cable

* One 18 Channel flexible electrode array from Sapien LLC

Cthulhu Shield

# Required Software
* [Arduino IDE](https://www.arduino.cc/en/Main/Software)
* This library (Directions on how to install below)

# Hardware Assembly:
Install Cthulhu Shield onto Arduino Uno or Arduino Mega and attach the USB cable and electrode array. 

# Example:
Open Arduino IDE. Once you have installed the Cthulhu Shield library (see 'Install Library' at end) go to **file**>**examples**>**Cthulhu-master** and open the **BareMinimum** example sketch.

example

Set your board and serial port from the **tools** dropdown menu and upload the sketch to your Arduino Uno or Mega.

example

example

The Serial Input example is ready to be uploaded.

example

After the example is uploaded, one electrode should be activated. 

# Install Library:

Right now, the easiest way to install the Cthulhu library is by downloading the Zip file from github, and manually adding it from the arduino 'sketch' dropdown menu.

Navigate to the Cthulhu repo main page and download the zip file.

zip

Open Arduino and select **Include Library** > **Add .ZIP Library** from the **Sketch** dropdown menu.

add library

Navigate to the zip file you downloaded and select it (probably your 'Downloads' folder). 

The library should now be installed.

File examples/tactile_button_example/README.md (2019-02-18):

## Using the Cthulhu Shield and Arduino Uno as a Tactile Button With Your Tongue

# Introduction:
This example shows how to use the Cthulhu Shield and tri-state function of the the arduino analog pins (A0-A5) to create a (somewhat intense) stimulus waveform on the tongue at 4 'button' locations, and to sense whether the tongue is in contact with each button. 

If the LED is active, the LED's representing an electrode should noticiably brighten when the tongue is in contact with the electrode. 

The long pulses used here were selected to maximize the change in brightness of the LED's during tongue contact. 

The example will output an analog reading for each of the six buttons to the serial terminal if desired.

# Required Materials:

* Cthulhu Shield

Cthulhu_Shield

* Arduino Uno or compatible clone

Cthulhu Shield

* USB A to B Cable

USB A to B Cable

* One 18 Channel flexible electrode array from Sapien LLC

Cthulhu Shield

# Required Software
* [Arduino IDE](https://www.arduino.cc/en/Main/Software)
* This library (Directions on how to install below)

# Hardware Assembly:
Install Cthulhu Shield onto Arduino Uno or Arduino Mega and attach the USB cable and electrode array. 

# Example:
Open Arduino IDE. Once you have installed the Cthulhu Shield library (see 'Install Library' at end) go to **file**>**examples**>**Cthulhu-master** and open the **tactile_button_example** example sketch.

example

Set your board and serial port from the **tools** dropdown menu and upload the sketch to your Arduino Uno or Mega.

example

example

example

After uploading to the arduino, when you place the 18 Channel flexible electrode array on your tongue and press with your tongue on the top, bottom, left, or right, if the LED is active, an electrode should noticiably brighten with your tongue in contact with the electrode. This example will output an analog reading, so if you'd like to view this reading, press the "serial monitor" icon on the top right side of arduino screen and the serial monitor will display those readings. 

# Install Library:

Right now, the easiest way to install the Cthulhu library is by downloading the Zip file from github, and manually adding it from the arduino 'sketch' dropdown menu.

Navigate to the Cthulhu repo main page and download the zip file.

zip

Open Arduino and select **Include Library** > **Add .ZIP Library** from the **Sketch** dropdown menu.

add library

Navigate to the zip file you downloaded and select it (probably your 'Downloads' folder). 

The library should now be installed.

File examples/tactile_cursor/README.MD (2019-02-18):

## Using the Cthulhu Shield and Arduino Uno to Send Keystrokes With Your Tongue!

# Introduction:

The Cthulhu Shield and electrode array can be used to sense whether or not your tongue is in contact with certain electrodes. Combined with the electrotactile ability of the Cthulhu Shield, this can be used to create 'virtual' tactile buttons that can be pressed with the tongue. With some minor software hacking of the Arduino, and use of Microsoft's accessibility tools, you can use the Cthulhu to control your computer cursor or type with your tongue!

This example will show you how to upload the example 'tactile_cursor.ino' sketch to an Arduino Uno with mounted Cthulhu Shield (and then hack the Arduino) to use your tongue to send '8''4''2''6' and '5' keystrokes to your computer. These keys can be used to control your computer cursor after enabling accessibility functions on your Mac or PC. You can also use the onscreen keyboard to type and send emails with your tongue!

Game_Control

# Required Materials:

* Cthulhu Shield

Cthulhu Shield
* Arduino Uno or Mega or compatible clone with Atmega16U2 as USB to UART converter (it sounds like older boards using the Atmega8U2 may also work)

Cthulhu Shield
* USB A to B Cable

USB A to B Cable

* One 18 Channel flexible electrode array from Sapien LLC

Cthulhu Shield

# Required Software:
* This library
* [Arduino IDE](https://www.arduino.cc/en/Main/Software)
* [Flip programmer](https://www.microchip.com/developmenttools/ProductDetails/flip)

# Hardware Assembly:
Install Cthulhu Shield onto Arduino Uno or Arduino Mega and attach the USB cable and electrode array. 

# PC Setup:
For setup on Windows, follow the instructions below. If you have a Mac, please see the section entitled [Mac Setup](#mac-setup) further down the page. 

Open Arduino IDE. Once you have installed the Cthulhu Shield library (see 'Install Library' at end) go to **file**>**examples**>**Cthulhu-master** and open the **tactile_cursor** example sketch.

example

Set your board and serial port from the **tools** dropdown menu and upload the sketch to your Arduino Uno or Mega.

example

example

example

Once you have downloaded the [Flip programmer](https://www.microchip.com/developmenttools/ProductDetails/flip), open the progam and select the ATmega16U2 device by selecting the IC icon in the upper left of the window. 

flipchipselect

With the Arduino powered, momentarily short these two pins together with a screwdriver or something metallic to put the ATmega16U2 into a state that allows to reprogram it.

Unohack

Click the USB cable icon in the upper left and select the 'USB' option from the dropdown. 

USB

Previously 'greyed-out' features in the window should now be available (if you can't connect and get an error message see section below titled 'Troubleshooting-Update Driver')

Select the Load HEX file button at the top of the window and navigate to and select the 'Arduino-keyboard-0.3.hex' file on your computer (located in the '16u2_firmware' folder of this example)

load hex

Once the firmware is selected, hit run to upload the new firmware to the ATmega16U2 chip on the Arduino.

run

**Now unplug your Arduino from your computer to remove power and plug it back in again. Your computer should now recognize the arduino as a standard keyboard.**

Click on your windows search bar and search for and open 'control panel'.
controlpanel

Select 'Ease of Access', and click 'Ease of Access' again in the window that opens.

ease1

ease2

Click **Make the mouse easier to use** and click the box to enable **Turn on mouse keys**.

mouse1

mouse2

We recommend adjusting the speed and acceleration of the mouse to higher settings. To do this, go back to the main **Make the mouse easier to use** menu and select **Set up mouse keys** (note, the box to enable mouse keys should already be enabled).

mouse3

Adjust the sliders as desired. We recommend max speed and medium-high acceleration.

mouse4

If you havent already, carefully lift the latch of the ZIF connector, insert the electrode array gold side down, and close the latch. 

Use the tip of your tongue to press the tactile 'buttons' on the electrodes at the front, back , and both sides of the array. The LED's on the Cthulhu Shield will change brightness when your tongue is contacting them, so look at them and move your tongue around to train up and practice. 

Use these buttons like a directional pad to move your cursor around the screen. Flatten your tongue against the array to press all electrodes to click. (click-hold/drag has not yet been implemented).

When you feel like it, enable the onscreen keyboard in the ease of access settings and type and email or novel. The predicted words suggessted at the top of the keyboard actual make typing pretty fast in most situations!

key1

key2

**Note: If you want your Arduino to act like a regular Arduino again (so you can load different sketches on it) you must short the pins together and repeat this process, selecting 'Arduino-usbserial-uno.hex' or 'Arduino-subserial-mega.hex'to put the standard Arduino firmware back onto the ATmega16U2.**

# Mac Setup:

# Going Further:

# Acknowledgments: 
Inspiration for this project and Firmware for Atmega16U2 came directly from coopermaa at https://github.com/coopermaa/USBKeyboard

# Troubleshooting-Update Driver:
If you get an error message when trying to connect to your device in Flip, you may need to update the driver in your device manager. 

Make sure you are running java Runtime Environment 32, then go to **device manager** on your computer, find the 16U2 device, 

16U2device

right click and select **properties** > **update drivers**, **browse my computer for driver software** and navigate to and select the **Flip folder** on your computer. 

16U2device2

16U2device2

16U2device2

Once the **Flip folder** has been selected, click **update drivers**.

16U2device2

# Install Library:

Right now, the easiest way to install the Cthulhu library is by downloading the Zip file from github, and manually adding it from the arduino 'sketch' dropdown menu.

Navigate to the Cthulhu repo main page and download the zip file.

zip

Open Arduino and select **Include Library** > **Add .ZIP Library** from the **Sketch** dropdown menu.

add library

Navigate to the zip file you downloaded and select it (probably your 'Downloads' folder). 

The library should now be installed.

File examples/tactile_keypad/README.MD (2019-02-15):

## Using the Cthulhu Shield and Arduino Uno to Send Keystrokes With Your Tongue!

# Introduction:

The Cthulhu Shield and electrode array can be used to sense whether or not your tongue is in contact with certain electrodes. Combined with the electrotactile ability of the Cthulhu Shield, this can be used to create 'virtual' tactile buttons that can be pressed with the tongue. With some minor software hacking of the Arduino, we can get the Arduino-Cthulhu to tell the computer that it is a keyboard and send keystrokes to your computer with your tongue.

This example will show you how to upload the example 'tactile_keypad.ino' sketch to an Arduino Uno with mounted Cthulhu Shield (and then hack the Arduino) to  use your tongue to send 'w''a''s''d' and 'space' keystrokes to your computer. These keys are the standard keys used to control character movement in many PC games, thus you will be able to move your character with your tongue as shown in the gif below.

Game_Control

# Required Materials:

* Cthulhu Shield

Cthulhu Shield
* Arduino Uno or Mega or compatible clone with Atmega16U2 as USB to UART converter (it sounds like older boards using the Atmega8U2 may also work)

Cthulhu Shield
* USB A to B Cable

USB A to B Cable

* One 18 Channel flexible electrode array from Sapien LLC

Cthulhu Shield

# Required Software:
* This library
* [Arduino IDE](https://www.arduino.cc/en/Main/Software)
* [Flip programmer](https://www.microchip.com/developmenttools/ProductDetails/flip)

# Hardware Assembly:
Install Cthulhu Shield onto Arduino Uno or Arduino Mega and attach the USB cable and electrode array. 

# Example:
Open Arduino IDE. Once you have installed the Cthulhu Shield library (see 'Install Library' at end) go to **file**>**examples**>**Cthulhu-master** and open the **tactile_keypad** example sketch.

example

Set your board and serial port from the **tools** dropdown menu and upload the sketch to your Arduino Uno or Mega.

example

example

example

Once you have downloaded the [Flip programmer](https://www.microchip.com/developmenttools/ProductDetails/flip), open the progam and select the ATmega16U2 device by selecting the IC icon in the upper left of the window. 

flipchipselect

With the Arduino powered, momentarily short these two pins together with a screwdriver or something metallic to put the ATmega16U2 into a state that allows to reprogram it.

Unohack

Click the USB cable icon in the upper left and select the 'USB' option from the dropdown. 

USB

Previously 'greyed-out' features in the window should now be available (if you can't connect and get an error message see section below titled 'Troubleshooting-Update Driver')

Select the Load HEX file button at the top of the window and navigate to and select the 'Arduino-keyboard-0.3.hex' file on your computer (located in the '16u2_firmware' folder of this example)

load hex

Once the firmware is selected, hit run to upload the new firmware to the ATmega16U2 chip on the Arduino.

run

**Now unplug your Arduino from your computer to remove power and plug it back in again. Your computer should now recognize the arduino as a standard keyboard.**

If you havent already, carefully lift the latch of the ZIF connector, insert the electrode array gold side down, and close the latch. Open a text editor and place the electrode array in your mouth to test it out. 

Use the tip of your tongue to press the tactile 'buttons' on the electrodes at the front, back , and both sides of the array. The LED's on the Cthulhu Shield will change brightness when your tongue is contacting them, so look at them and move your tongue around to train up and practice. 'w', 'a', 's', and 'd' keystrokes are mapped to the front, left, back, and right electrodes respectively. A 'space' keystroke can be sent by flattening your tongue against the array and pressing all the electrodes simultaneously. 

When you feel like it, fire up your favorite game with 'wasd' motion control and try controlling your character with your tongue!

**Note: If you want your Arduino to act like a regular Arduino again (so you can load different sketches on it) you must short the pins together and repeat this process, selecting 'Arduino-usbserial-uno.hex' or 'Arduino-subserial-mega.hex'to put the standard Arduino firmware back onto the ATmega16U2.**

# Going Further:

Change the keystrokes used in the example to something that you prefer! Maybe you want to hotkey certain actions to your tongue to give you an edge while gaming. If you have a disability, maybe there are other keystrokes that suit your needs better! 

Have fun, and if you make something cool, share it with us!

# Acknowledgments: 
Inspiration for this project and Firmware for Atmega16U2 came directly from coopermaa at https://github.com/coopermaa/USBKeyboard

# Troubleshooting-Update Driver:
If you get an error message when trying to connect to your device in Flip, you may need to update the driver in your device manager. 

Make sure you are running java Runtime Environment 32, then go to **device manager** on your computer, find the 16U2 device, 

16U2device

right click and select **properties** > **update drivers**, **browse my computer for driver software** and navigate to and select the **Flip folder** on your computer. 

16U2device2

16U2device2

16U2device2

Once the **Flip folder** has been selected, click **update drivers**.

16U2device2

# Install Library:

Right now, the easiest way to install the Cthulhu library is by downloading the Zip file from github, and manually adding it from the arduino 'sketch' dropdown menu.

Navigate to the Cthulhu repo main page and download the zip file.

zip

Open Arduino and select **Include Library** > **Add .ZIP Library** from the **Sketch** dropdown menu.

add library

Navigate to the zip file you downloaded and select it (probably your 'Downloads' folder). 

The library should now be installed.

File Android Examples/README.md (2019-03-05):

Cthulhu Android Examples
========================
This folder contains source code for several example applications that show how to use the Cthulhu Shield with an Android device. APKs for each app are provided in thier respective folders, and the apps are also available for download on the Google Play Store. 

The source code contianed here is provided as-is, and is meant purely for demonstration.  

These applications were developed by Marco Martinez ([Funkatronics](https://github.com/funkatronics "Funkatronics GitHub")), with support from Sapien, LLC.

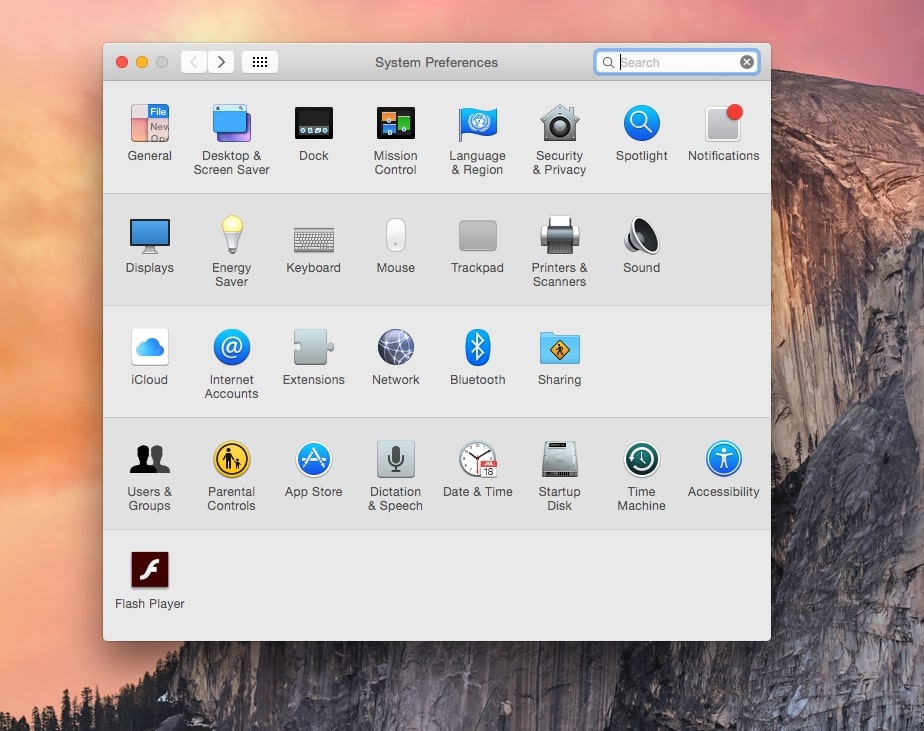
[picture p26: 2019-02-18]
jpgs/Cursor 2 - System Preferences.jpg

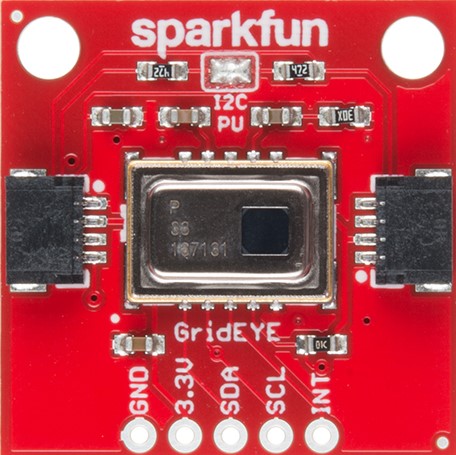
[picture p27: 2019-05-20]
jpgs/converter.jpg

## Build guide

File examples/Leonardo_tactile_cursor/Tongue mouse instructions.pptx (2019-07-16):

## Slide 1

Up

Right

Use the tip of your tongue to touch different electrodes

Left

Down

Touching and holding different electrodes will cause the computer cursor to move in that direction.

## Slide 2

Press and hold the tip of your tongue to the back two electrodes to move the cursor up!

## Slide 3

Press and hold the tip of your tongue to the front two electrodes to move the cursor down!

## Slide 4

Press and hold the tip of your tongue to the left electrode to move the cursor left!

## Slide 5

Press and hold the tip of your tongue to the right electrode to move the cursor right!

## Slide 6

Flatten your tongue against the array to touch electrodes then remove your tongue from the array to click! Do this twice quickly to double click!

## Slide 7

Hold Your tongue against all electrodes for 2 seconds to Right Click!

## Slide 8

Hold Your tongue against all electrodes, and without moving your tongue off the array, slide your tongue to a directional electrode to click and drag!

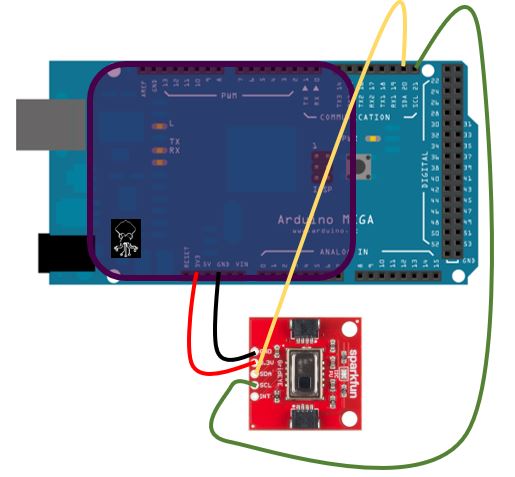
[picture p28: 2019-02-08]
jpgs/heatcammegasetup.JPG

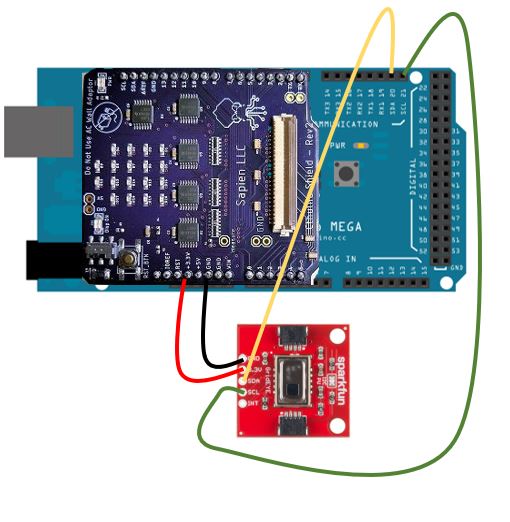
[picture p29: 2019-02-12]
jpgs/infrared_setup.JPG

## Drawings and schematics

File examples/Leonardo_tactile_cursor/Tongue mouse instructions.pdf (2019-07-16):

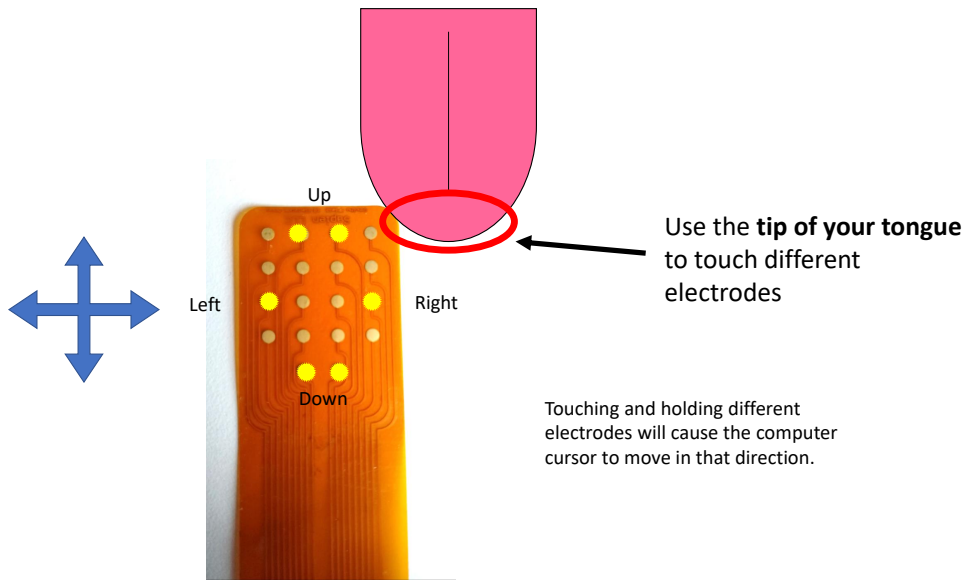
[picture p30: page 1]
Down; Left; Right

Use the tip of your tongue
to touch different
electrodes

Touching and holding different
electrodes will cause the computer
cursor to move in that direction.

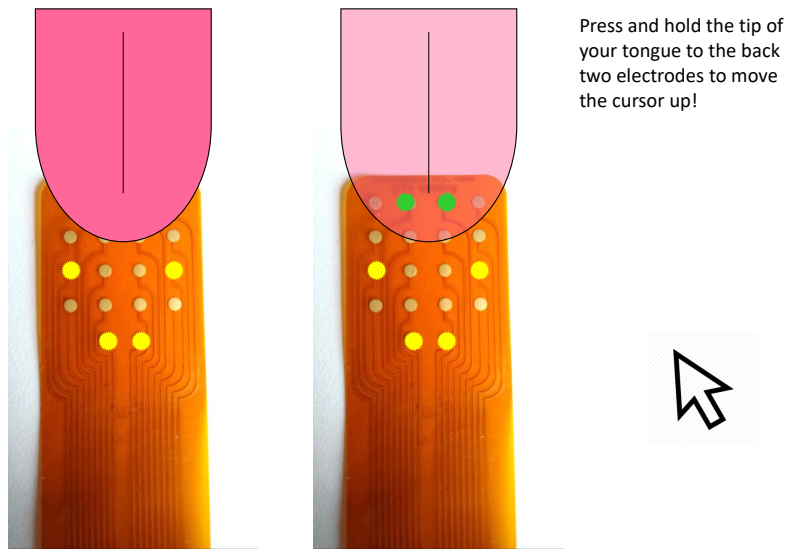
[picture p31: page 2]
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

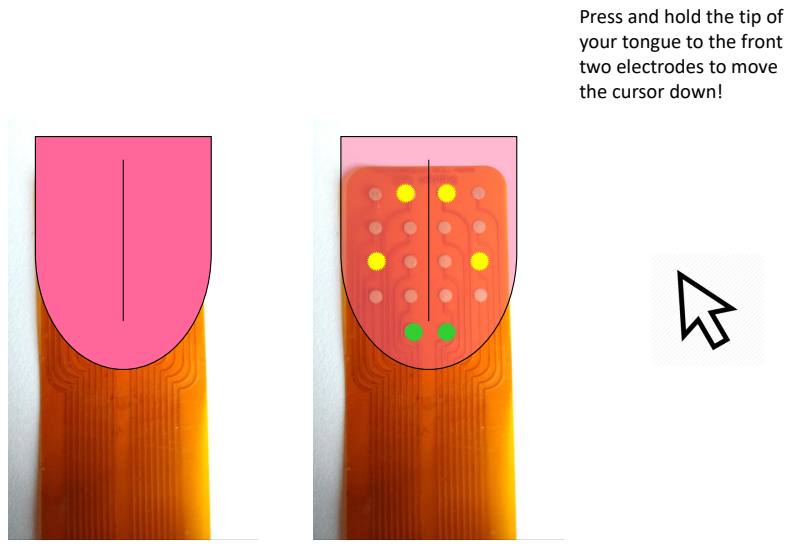
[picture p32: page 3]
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

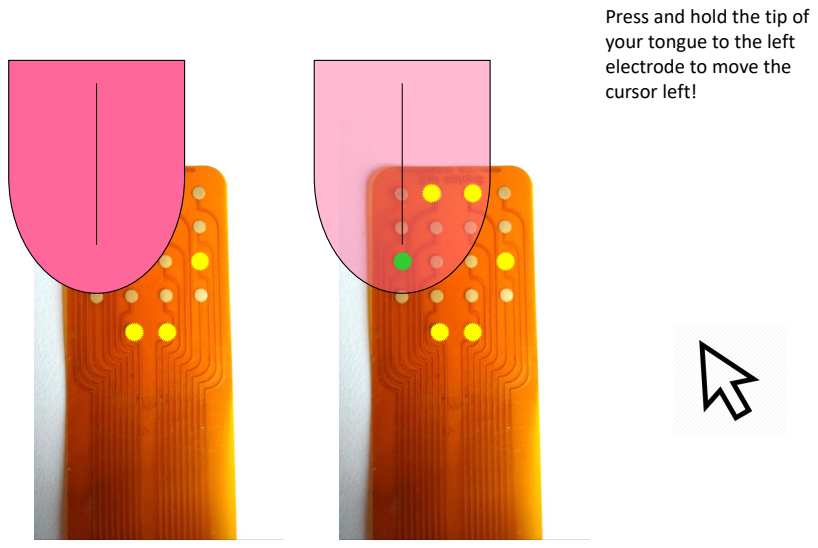
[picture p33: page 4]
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

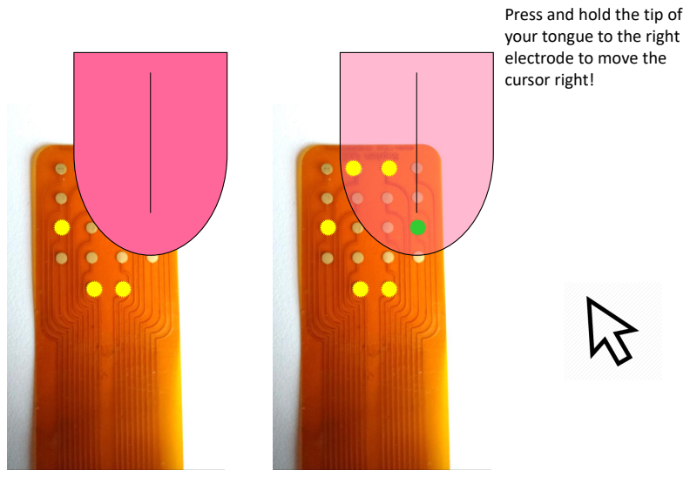
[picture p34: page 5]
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

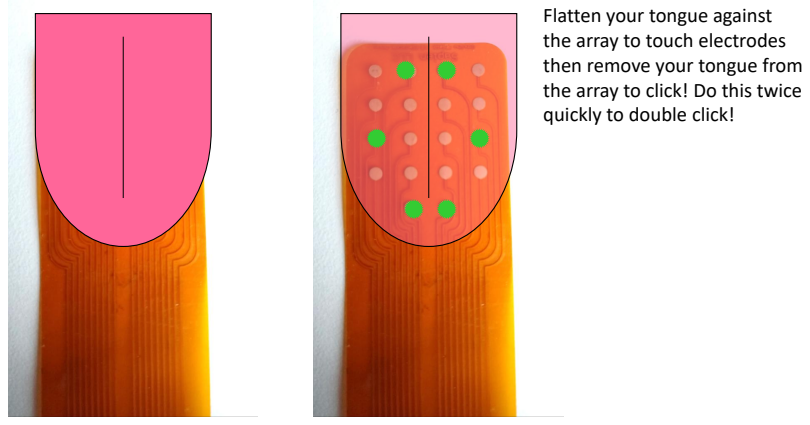
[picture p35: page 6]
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

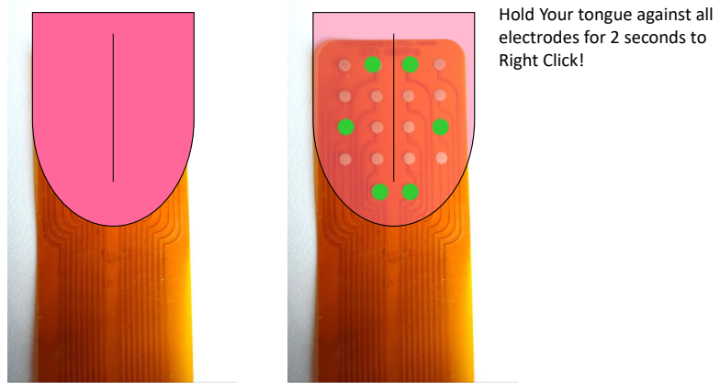
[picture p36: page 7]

Hold Your tongue against all
electrodes for 2 seconds to
Right Click!

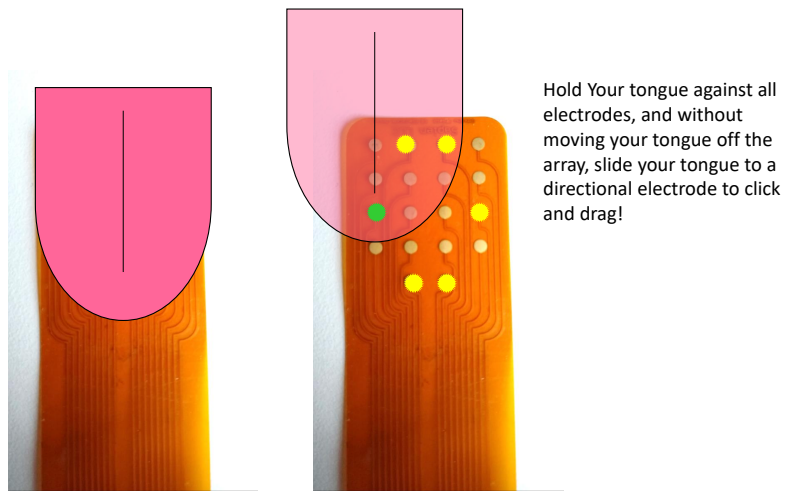
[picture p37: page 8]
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

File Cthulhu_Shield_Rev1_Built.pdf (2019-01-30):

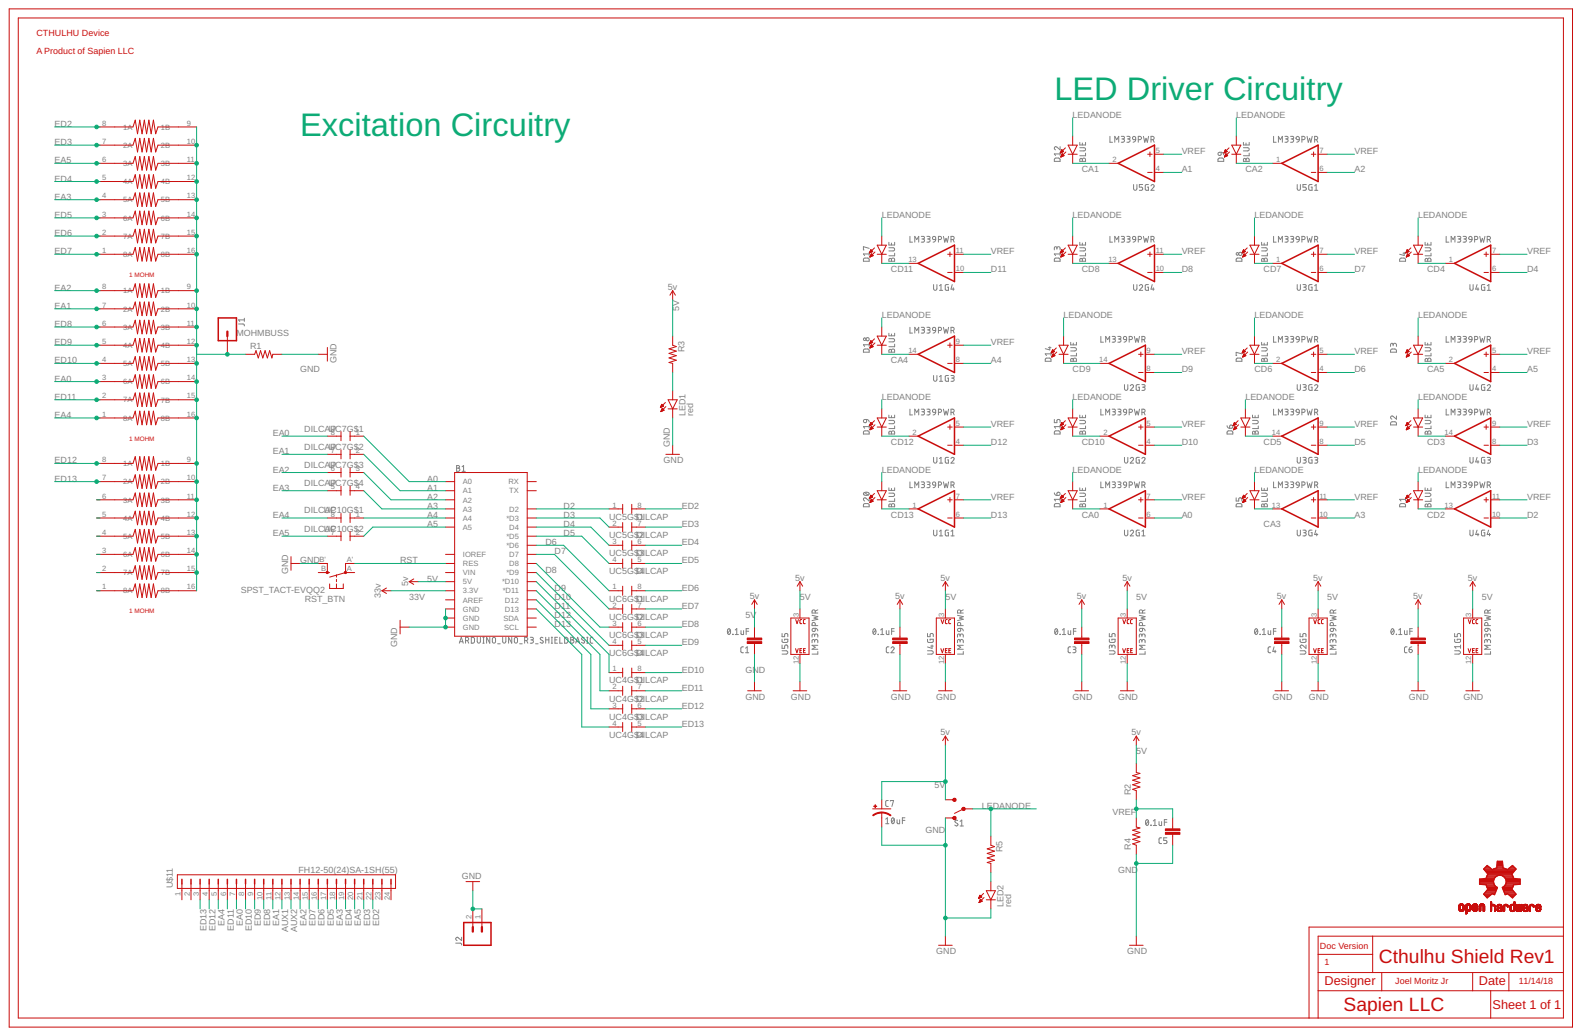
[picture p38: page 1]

A Product of Sapien LLC

GND
DILCAP DILCAP DILCAP

DILCAP DILCAP DILCAP DILCAP

DILCAP DILCAP

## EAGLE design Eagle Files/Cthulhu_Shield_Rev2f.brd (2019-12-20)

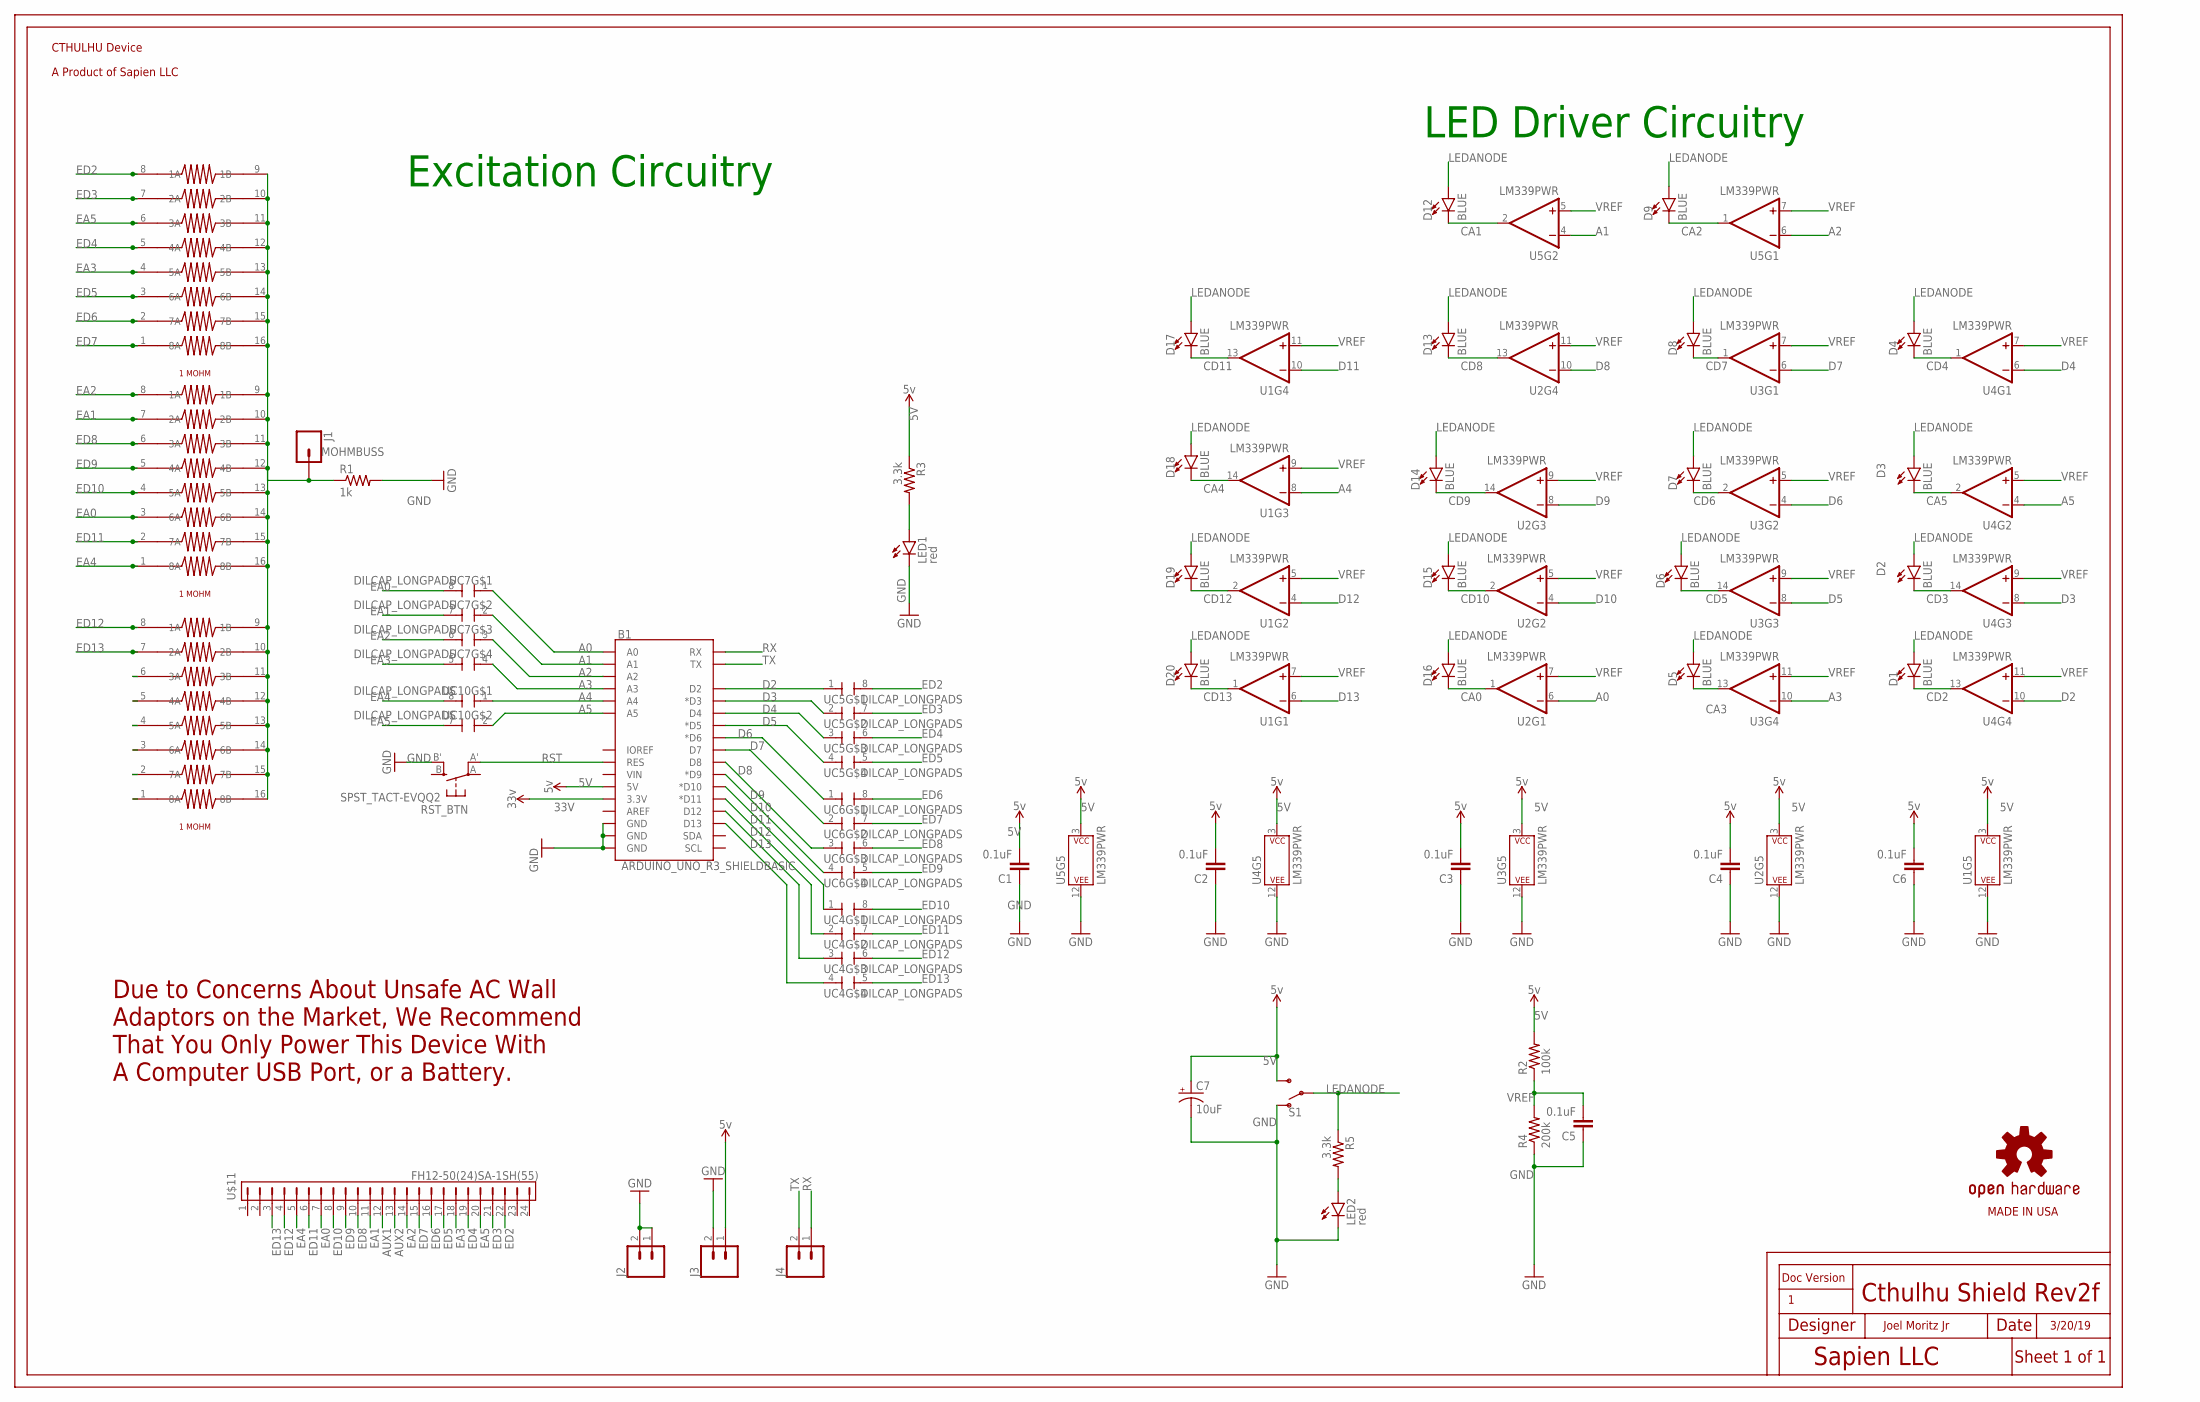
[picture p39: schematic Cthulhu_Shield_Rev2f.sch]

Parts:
B1: ARDUINO_UNO_R3_SHIELDBASIC; UNO_R3_SHIELD
C1, C2, C3, C4, C5, C6: 0.1uF; 0603
C7: 10uF; EIA3528
D1, D2, D3, D4, D5, D6, D7, D8, D9, D12, D13, D14, D15, D16, D17, D18, D19, D20: BLUE; LED-0603
J1: CONN_01; 1X01
J2, J3, J4: CONN_02; 1X02
LED1, LED2: red; LED-1206
LOGO1: OSHW-LOGOL; OSHW-LOGO-L
R1: 1k; 0402
R2: 100k; 0402
R3, R5: 3.3k; 0402
R4: 200k; 0402
RST_BTN: SPST_TACT-EVQQ2; EVQ-Q2
S1: SWITCH-SPDT-SMD-AYZ0202; SWITCH_DPDT_SMD_AYZ0202
U1, U2, U3, U4, U5: LM339PWR; TSSOP-14
U$1, U$2, U$3: 1MOHM8; JJ_CUSTOM_PARTS_1MOHMARRAY
U$4: NO_WALL_ADAPTOR
U$5: MADEINUSA
U$8: SAPEIN_LOGO_BOTTOM; SAPIEN_LOGO_BOTTOM
U$9: CTHULHU_LOGO; CTHULHU
U$11: FH12-50(24)SA-1SH(55); FH12-16S-1SH
UC4, UC5, UC6, UC7, UC10: DILCAP_LONGPADS; RESISTOR-DIL_4X0402ARV341_LONGPADS

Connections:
5V: B1.5V, C1.2, C2.2, C3.2, C4.2, C6.2, C7.A (+), J3.1, R2.2, R3.1, S1.3 (S), U1.3 (P$V+), U2.3 (P$V+), U3.3 (P$V+), U4.3 (P$V+), U5.3 (P$V+)
33V: B1.3.3V
A0: B1.A0, U2.6 (-IN), UC7.1
A1: B1.A1, U5.4 (-IN), UC7.2 (1)
A2: B1.A2, U5.6 (-IN), UC7.3 (1)
A3: B1.A3, U3.10 (-IN), UC7.4 (1)
A4: B1.A4, U1.8 (-IN), UC10.1
A5: B1.A5, U4.4 (-IN), UC10.2 (1)
AUX1: U$11.12
AUX2: U$11.13
CA0: D16.C, U2.1 (OUT)
CA1: D12.C, U5.2 (OUT)
CA2: D9.C, U5.1 (OUT)
CA3: D5.C, U3.13 (OUT)
CA4: D18.C, U1.14 (OUT)
CA5: D3.C, U4.2 (OUT)
CD2: D1.C, U4.13 (OUT)
CD3: D2.C, U4.14 (OUT)
CD4: D4.C, U4.1 (OUT)
CD5: D6.C, U3.14 (OUT)
CD6: D7.C, U3.2 (OUT)
CD7: D8.C, U3.1 (OUT)
CD8: D13.C, U2.13 (OUT)
CD9: D14.C, U2.14 (OUT)
CD10: D15.C, U2.2 (OUT)
CD11: D17.C, U1.13 (OUT)
CD12: D19.C, U1.2 (OUT)
CD13: D20.C, U1.1 (OUT)
D2: B1.D2, U4.10 (-IN), UC5.1
D3: B1.D3 (*D3), U4.8 (-IN), UC5.2 (1)
D4: B1.D4, U4.6 (-IN), UC5.3 (1)
D5: B1.D5 (*D5), U3.8 (-IN), UC5.4 (1)
D6: B1.D6 (*D6), U3.4 (-IN), UC6.1
D7: B1.D7, U3.6 (-IN), UC6.2 (1)
D8: B1.D8, U2.10 (-IN), UC6.3 (1)
D9: B1.D9 (*D9), U2.8 (-IN), UC6.4 (1)
D10: B1.D10 (*D10), U2.4 (-IN), UC4.1
D11: B1.D11 (*D11), U1.10 (-IN), UC4.2 (1)
D12: B1.D12, U1.4 (-IN), UC4.3 (1)
D13: B1.D13, U1.6 (-IN), UC4.4 (1)
EA0: U$2.3 (6A), U$11.7, UC7.8 (2)
EA1: U$2.7 (2A), U$11.11, UC7.7 (2)
EA2: U$2.8 (1A), U$11.14, UC7.6 (2)
EA3: U$1.4 (5A), U$11.18, UC7.5 (2)
EA4: U$2.1 (8A), U$11.5, UC10.8 (2)
EA5: U$1.6 (3A), U$11.20, UC10.7 (2)
ED2: U$1.8 (1A), U$11.22, UC5.8 (2)
ED3: U$1.7 (2A), U$11.21, UC5.7 (2)
ED4: U$1.5 (4A), U$11.19, UC5.6 (2)
ED5: U$1.3 (6A), U$11.17, UC5.5 (2)
ED6: U$1.2 (7A), U$11.16, UC6.8 (2)
ED7: U$1.1 (8A), U$11.15, UC6.7 (2)
ED8: U$2.6 (3A), U$11.10, UC6.6 (2)
ED9: U$2.5 (4A), U$11.9, UC6.5 (2)
ED10: U$2.4 (5A), U$11.8, UC4.8 (2)
ED11: U$2.2 (7A), U$11.6, UC4.7 (2)
ED12: U$3.8 (1A), U$11.4, UC4.6 (2)
ED13: U$3.7 (2A), U$11.3, UC4.5 (2)
GND: B1.GND@0 (GND), B1.GND@1 (GND), B1.GND@2 (GND), C1.1, C2.1, C3.1, C4.1, C5.1, C6.1, C7.C (-), J2.1, J2.2, J3.2, LED1.C, LED2.C, R1.2, R4.1, RST_BTN.B' (S1), S1.1 (O), U1.12 (P$V-), U2.12 (P$V-), U3.12 (P$V-), U4.12 (P$V-), U5.12 (P$V-)
LEDANODE: D1.A, D2.A, D3.A, D4.A, D5.A, D6.A, D7.A, D8.A, D9.A, D12.A, D13.A, D14.A, D15.A, D16.A, D17.A, D18.A, D19.A, D20.A, R5.1, S1.2
MOHMBUSS: J1.1, R1.1, U$1.9 (1B), U$1.10 (2B), U$1.11 (3B), U$1.12 (4B), U$1.13 (5B), U$1.14 (6B), U$1.15 (7B), U$1.16 (8B), U$2.9 (1B), U$2.10 (2B), U$2.11 (3B), U$2.12 (4B), U$2.13 (5B), U$2.14 (6B), U$2.15 (7B), U$2.16 (8B), U$3.9 (1B), U$3.10 (2B), U$3.11 (3B), U$3.12 (4B), U$3.13 (5B), U$3.14 (6B), U$3.15 (7B), U$3.16 (8B)
unnamed: LED1.A, R3.2
unnamed: LED2.A, R5.2
RST: B1.RES, RST_BTN.A' (P1)
RX: B1.RX, J4.1
TX: B1.TX, J4.2
VREF: C5.2, R2.1, R4.2, U1.5 (+IN), U1.7 (+IN), U1.9 (+IN), U1.11 (+IN), U2.5 (+IN), U2.7 (+IN), U2.9 (+IN), U2.11 (+IN), U3.5 (+IN), U3.7 (+IN), U3.9 (+IN), U3.11 (+IN), U4.5 (+IN), U4.7 (+IN), U4.9 (+IN), U4.11 (+IN), U5.5 (+IN), U5.7 (+IN)

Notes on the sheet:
Doc Version
Designer
Date
Sheet 1 of 1
Cthulhu Shield Rev2f
Joel Moritz Jr
3/20/19
Sapien LLC
LED Driver Circuitry
Excitation Circuitry

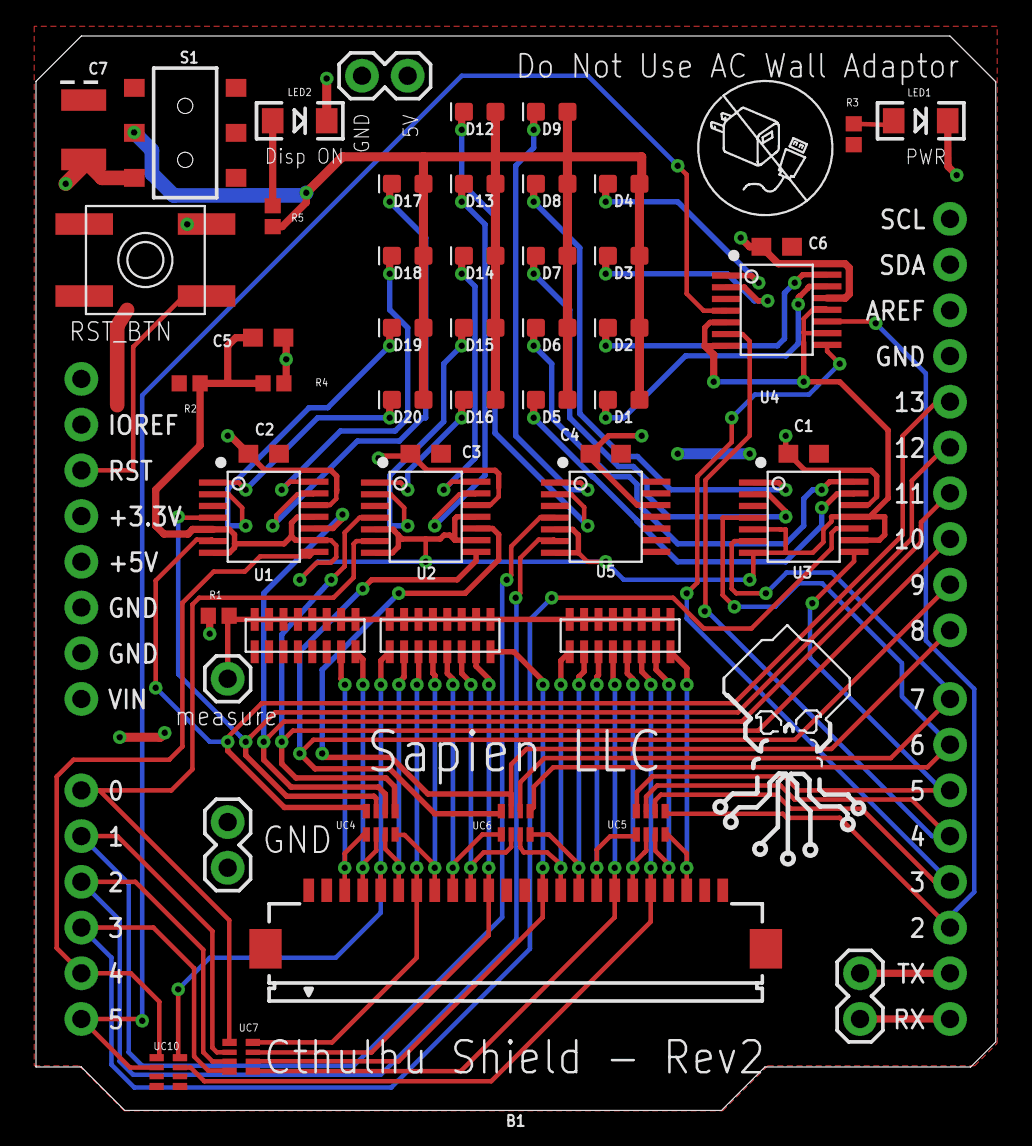
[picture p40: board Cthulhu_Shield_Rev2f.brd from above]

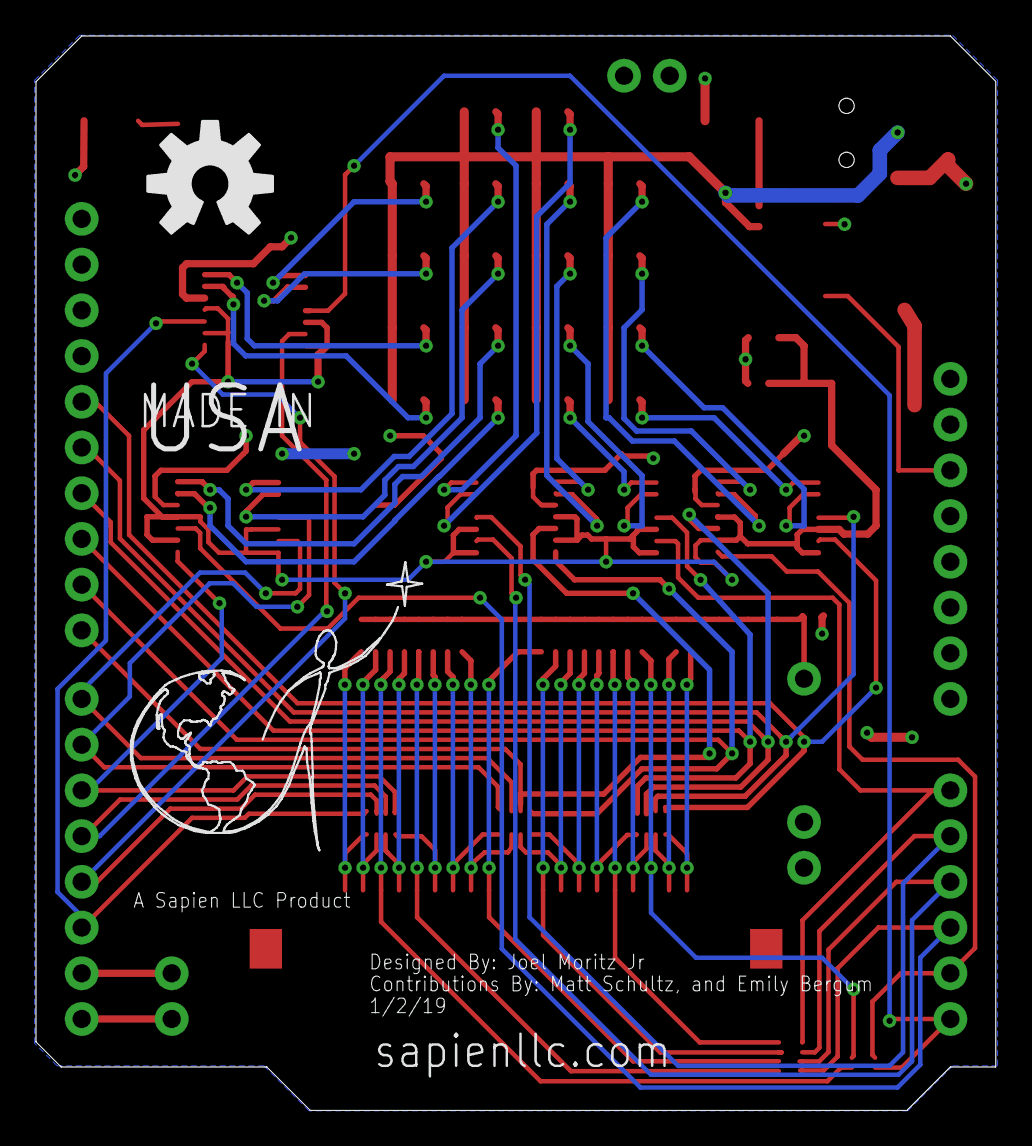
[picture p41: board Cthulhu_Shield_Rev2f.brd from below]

Board: 2 copper layers, 53.3 x 59.7 mm, 58 parts (2 on the bottom side), 64 nets.

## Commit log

2019-02-08 Edited new material
    smol edits
2019-02-10 Firmware for Atmega16U2
    Wanted local copies in case coopermaa ever deletes his repo.
2019-02-22 accelerometer_Cthulhu_example
    Arduino code, README, and jpgs
2019-03-07 force_sensitve_resistor_example
    arduino code, README, and jpgs
2019-05-11 Leonardo Mouse Code
    Code to use a Cthulhu Shield and arduino Leonardo as a full function computer mouse. Includes right click, and click drag functions, no hardware hacks, or computer settings need to be changed. Direct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
2019-05-20 Updated infrared camera README
2019-07-16 Heat cam updated
2019-12-20 Eagle files added
    [Cthulhu_Shield_Rev2f.brd, Cthulhu_Shield_Rev2f.sch]

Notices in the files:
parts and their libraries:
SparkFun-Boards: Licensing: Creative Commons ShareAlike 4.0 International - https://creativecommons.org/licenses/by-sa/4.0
